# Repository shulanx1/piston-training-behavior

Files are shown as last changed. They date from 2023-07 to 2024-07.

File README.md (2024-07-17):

# README #

* Behavioral training set up for two whisker discrimination task based on pneumetic whisker stimulation

### Python environment Requirement: ###
* numpy
* scipy
* playsound
* pyserial

### Hardware on the circuit board: ###
* 24 V piston air pressure regulator: https://www.smcpneumatics.com/V114T-5LZ-M5.html
* 24 VDC power relay: digikey 255-5324-5-ND
* dual channel diod: digikey 1655-BAT54CCT-ND
* dual channel NTN transister: digikey MBT3904DW1T1G
* 12 V water valve: Nresearch 161K011 or thevalveshop 411L3112HV https://www.thevalveshop.com/menu/auto/asco/asco-scientific.html 
* 12 V water valve driver: Nresearch 161D1X250
* 5V speaker (with amplifier): digikey 1528-1746-ND
* vibration motor: 3V
* stepper motor: Makeblock Me Stepper Motor Driver https://amicus.com.sg/shop/makeblock/me-stepper-motor-driver/
* rotary encoder: https://www.usdigital.com/products/encoders/incremental/rotary/shaft/H5
* piezo based lickometer:<br />
single-rail op-amp: TLV2771CDBVR<br />
shunt regulator: ATL431BQDBZR<br />
non-inverting svhmitt trigger: SN74LVC1G17DBVR<br />
LED: 160-1183-1-ND<br />
trimmer resistor: digikey 3362P-504LF-ND<br />
* piezo based lickometer (with rail splitter:<br />
op-amp: TLV2371IDBVR<br />
rail splitter: TLE2426QDRG4Q1 <br />
cap 200nF: 1189-2375-ND  <br />
cap 1uF: 399-ESS105M050AB2EACT-ND <br\>

### pin layout V6 ###
* D2: capacitance/piezo lick sensor
* D3: water valve
* D5, D6: rotary encoder (A,B)
* D8, D9, D11, D12: piston
* D10: sliding switch (start trigger)
* A1, A2: LED/conductance lick sensor
* A3: speaker
* D11, D7: stepper motor (STP, DIR)
* D4, D12: vibrating piezo

### pin layout V7 ###
* D2: capacitance/piezo lick sensor
* D3: water valve
* D4: sliding switch (start trigger)
* D5, D6, A2: rotary encoder (A,B,rotations)
* D8, D9, A4, A5: piston
* A1: LED/conductance lick sensor
* A3: speaker
* A5, A4: stepper motor (STP, DIR)

### Files ###

* //BehavioralPCB: arduino code to upload to arduino uno (board V6)
* //Bonsai lick detection: real time lick detection with webcam when capactive based lick sensor causes electrical artifact
* //training.py: training file to serial communicate with arduino
* //behavior_training_decode: matlab file to decode the serial output of arduino
* //Arduino_board_V6: PCB design
* //CAD: laser engraving pattern on the running disk

### Install ###
* Arduino: <br />
At sketch -> include library -> add .zip library, add the dio2.zip folder<br />

* Python: <br />
on the command window, run: <br />
-- pip install playsound <br />
-- pip install pyserial <br />

### To start the training from command window ###
-- cd path-to-base-folder <br />
-- python training.py COM12 ear-tag-number phase <br />

### Training phase ###
* 1: no whisker stim, reward dispense when the lick is detected
* 2: GO and NOGO stim, with teaching signal
* 3: GO and NOGO stim, reward is given at "hit", time out at false alarm
* 4: optogenetic stimulation in randomly chosen half of the trials,  reward is given at "hit", time  out at false alarm

### Arduino test serial command ###
* 'v': test valve
* 'p': test pistons
* 'c': test cue sound
* 'f': flush the valve
* 'g': GO piston, use the sliding switch to turn on and off
* 'n': NOGO piston, use the sliding switch to turn on and off

### Arduino serial output row ###
* 1: rotary decoder
* 2: licking
* 3: valve
* 4: GO piston
* 5: NOGO piston
* 6: hit rate
* 7: false alarm rate
* 8: time

### Arduino pin map ###
* DO2: lick sensor
* DO3: valve
* DO5&DO6: rotary encoder
* D8, D9, D12, D12: pistons
* D10: sliding switch
* D13: trigger

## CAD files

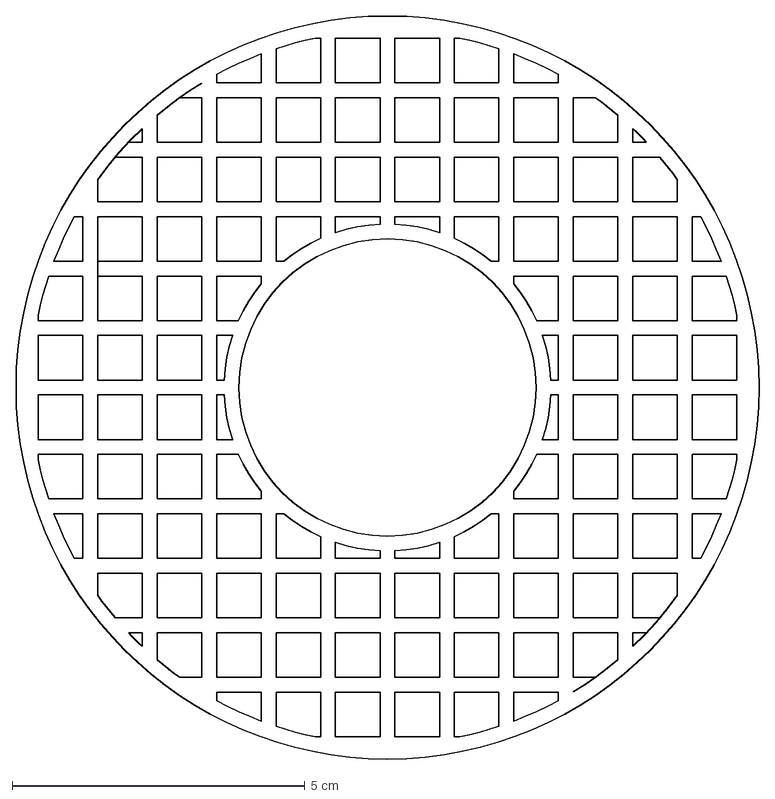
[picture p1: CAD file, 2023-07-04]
CAD/wheel v4.dxf
12.7 x 12.7 cm

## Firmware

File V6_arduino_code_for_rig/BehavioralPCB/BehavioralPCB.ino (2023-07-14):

/* Read Quadrature Encoder
   Connect Encoder to Pins encoder0PinA, encoder0PinB, and +5V.

*/
//print sequence: rundist, lick, valve, pistonGO, pisktonNOGO, time

#include <arduino2.h>

int val;
const int lick_sensor = 2;
const int valve_enable = 3;
const int pistonGO = 8;
const int output_trig = 13;
const int pistonNOGO = 9;
int encoder0PinA = 6;
int encoder0PinB = 5;
//int encoder0Pos = 0;
long int encoder0PosTot = 0;
int encoder0PinALast = LOW;
int n = LOW;
int count = 0;
int counter = 250;
int LED1 = A1;
int audio = A3;
int trigger = 10;
int lick_state = 0;
int valve_state = 0;
int go_stim_state = 0;
int nogo_stim_state = 0;
int go_teach = 0;
int nogo_teach = 0;
int previousState = LOW;
int piston_test_previousState = LOW;
int LED2 = A2;
int flag = 0;
int piston_test_flag = 0;
const int respond_window = 1000;  // time window (ms) after sensory stimuli that if lick is detected reward will be given
const int baseline_time = 3000;  // duration of baseline aquisition before trial starts
const int poststim_time = 4000;
const int reward_dur = 35;   // duration (ms) of reward
const int stim_dur = 4000; // time duration (ms) of sensory stimuli
const int time_out_dur = 15000;  // time out duration (ms)
const int wait_dur = 800;    //1000-sample time (us)
const int teach_dur = 10000; // small time out after teach signal, if lick happens during the time, considered as hit
float teach_ratio = 1.0;  //if correct detection/rejection is lower than teach ratio, send a teaching signal
const int previous_state_num = 10; //average the performance of previous numbers of trials to generate teach signals
unsigned int previous_go_performance = 992; //0x03e0
unsigned int previous_nogo_performance = 31;  //0x001f
unsigned int hit_trials = 0;
unsigned int fa_trials = 0;
unsigned int GO_trials = 0;
unsigned int NOGO_trials = 0;
float hit_rate = 0.0;
float fa_rate = 0.0;
const unsigned int update_shift = 15360; // 0x3c00, inverse the first 3rd to 6th digit, so the updated value is not the same as before 

const int cue_f = 2000;
const int cue_fs = 20000;
float cue_samples[100];
unsigned int cue_interval = 1000000/cue_fs;

int sampEncoderPos = 0;
int sampEncoderPosPrev = 0;
int changePos = 0;
unsigned long sampTime = 0;
int encoder_flag = 0;
float totalPos = 0;
const int fs_encoder = 100; // the sampling frequency of the encoder 

unsigned long microsStart;
unsigned long microsFix;
unsigned long deltaT;
float convertPos;

void setup() {
  Serial.begin(115200);  
//  Serial.setTimeout(1);
  while (!Serial) {
    //wait for serial port to open
  }
  pinMode (output_trig, OUTPUT);
  pinMode (encoder0PinA, INPUT);
  pinMode (encoder0PinB, INPUT);
  pinMode (lick_sensor, INPUT);
  pinMode (valve_enable, OUTPUT);
  pinMode (pistonGO, OUTPUT);
  pinMode (pistonNOGO, OUTPUT);
  pinMode (trigger, INPUT);
  pinMode (LED1, OUTPUT);
  pinMode(LED2,OUTPUT);
  pinMode(audio, OUTPUT);
  digitalWrite2(valve_enable,LOW);
  digitalWrite2(pistonGO, LOW);
  digitalWrite2(pistonNOGO, LOW);
  digitalWrite2(output_trig, LOW);

  float cue_time = 0.0;
  int cue_cycle = (int) (cue_fs/cue_f);
  for (int n = 0; n < cue_cycle; n++){
    cue_time = (float) n/cue_cycle;
    cue_samples[n] = (float)(127.0*sin(2*3.14*cue_time)+127.0);
  }  

  cli(); // stop interrupts
  
  // set TIMER1 interrupt at 2kHz
  TCCR1A = 0;// set entire TCCR1A register to 0
  TCCR1B = 0;// same for TCCR1B
  TCNT1  = 0;//initialize counter value to 0
  // set compare match register for 0.5kHz increments
  OCR1A  = 19999; //(16*10^6) / (fs_encoder*8) - 1 //(must be <65536)
  // turn on CTC mode
  TCCR1B |= (1 << WGM12);
  // Set CS10 and CS12 bits for 8 prescaler
  TCCR1B |= (1 << CS11) | (0 << CS10);  
  // enable timer compare interrupt
  TIMSK1 |= (1 << OCIE1A); 

  sei(); // allow interrupts

  previousState = digitalRead2(trigger);
  microsStart=micros();
  flag = 0;
  Serial.print("Ready");
}

void loop() {
  if((previousState == LOW) && (digitalRead2(trigger) == HIGH)){
    flag = 1;
    digitalWrite2(LED2,HIGH);
    microsFix = micros();
    previousState = HIGH;
    Serial.print("start");
    Serial.print("\n");
    while (!Serial.available());
    char a = Serial.read();
    teach_ratio = int (a-'0')/10.0;    
//    Serial.print(teach_ratio);
//    Serial.print('\n');    
    serialFlush();

  }
  else if((previousState == HIGH) && (digitalRead2(trigger) == LOW)){
      flag = 0;
      digitalWrite2(LED2,LOW);
      convertPos = 0;
      totalPos = 0;
      encoder0PosTot = 0;
      hit_trials = 0;
      fa_trials = 0;
      GO_trials = 0;
      NOGO_trials = 0;
      hit_rate = 0.0;
      fa_rate = 0.0;
      
      previousState = LOW;
      teach_ratio = 1;
  }

  if (flag == 1){
    if (Serial.available() > 0){
      char a = Serial.read();
      switch(a)
      {
        case '0':   // reward given whenever lick happens
          if (digitalRead2(lick_sensor) == HIGH){
            lick_state = 1;
            valve_state = 1;
            digitalWrite2(valve_enable, HIGH);
            delay(reward_dur);
            digitalWrite2(valve_enable, LOW);
            rotary_decode();
            valve_state = 0;
            while (digitalRead2(lick_sensor)==HIGH){
              delay(5);
              lick_state = 1;
              rotary_decode();
          } 
          }
          lick_state = 0;
          valve_state = 0;
          rotary_decode();
          break;

        case '1':   
        /* GO stimuli, 
        if the average mistake in the previous 10 trials larger than 0.5, give reward regardless of licking, 
        otherwise, reward only when licking */
          digitalWrite2(output_trig, LOW);
          GO_trials = GO_trials + 1;
          count = 0;
            while (count < baseline_time){
            if (digitalRead2(lick_sensor)==HIGH){
              lick_state = 1;
            }
            else{lick_state = 0;}
            rotary_decode();
            delayMicroseconds(wait_dur);
            count = count + 1;
          }   //baseline
          count = 0;
          digitalWrite2(pistonGO, HIGH);
          go_stim_state = 1;
          count = 0;
          delay(10); // time for piston response
          previous_go_performance = ((previous_go_performance << 1) ^ update_shift) & 16383; // left shift, inverse 3rd to 6th digit, zero 1st &2nd digit
          while (count < stim_dur-10){
            if (digitalRead2(lick_sensor)==HIGH){
              lick_state = 1;
              previous_go_performance = previous_go_performance | 1;
            }
            else{
              lick_state = 0;
            }
            rotary_decode();
            delayMicroseconds(wait_dur);
            count = count + 1;
          }
          digitalWrite2(pistonGO, LOW);
          go_stim_state = 0;         
          if (previous_go_performance & 1 == 1){
            hit_trials = hit_trials + 1;
            rotary_decode();
            valve_state = 1;
            digitalWrite2(valve_enable, HIGH);
            delay(reward_dur);
            digitalWrite2(valve_enable, LOW);  
            rotary_decode();
            hit_rate = (float) hit_trials/GO_trials;
          }
          else {
          go_teach_signal();
          hit_rate = (float) hit_trials/GO_trials;
          if ((go_teach == 1)){
            rotary_decode();
            valve_state = 1;
            digitalWrite2(valve_enable, HIGH);
            delay(reward_dur);
            digitalWrite2(valve_enable, LOW);   
            rotary_decode();
            previous_go_performance = previous_go_performance | (1 << 15);
            while (count < teach_dur){ // small time out session after teach signal
              if (digitalRead2(lick_sensor)==HIGH){
                lick_state = 1;
                previous_go_performance = previous_go_performance | 1;
                //hit_rate = (float) (hit_trials+1)/GO_trials;
              }
              else{lick_state = 0;}
            rotary_decode();
            delayMicroseconds(wait_dur);
            count = count + 1;
            }
            if (previous_go_performance & 1 == 1){
              hit_trials = hit_trials + 1;
            }
            hit_rate = (float) (hit_trials)/GO_trials;
            serialFlush();
          }
            }
                
          rotary_decode(); 
          
          lick_state = 0;
          count = 0;
            while (count < poststim_time){
            if (digitalRead2(lick_sensor)==HIGH){
              lick_state = 1;
            }
            else{lick_state = 0;}
            rotary_decode();
            delayMicroseconds(wait_dur);
            count = count + 1;
          }   //baseline
          valve_state = 0;  
          digitalWrite2(output_trig, LOW);
          
          break;
        
        case '7':   
        /* NOGO stimuli, 
        if the average mistake in the previous 10 trials larger than 0.5, no time out regardless of licking, 
        otherwise, timeout when licking */
          NOGO_trials = NOGO_trials + 1;
          digitalWrite2(output_trig, HIGH);
          count = 0;
            while (count < baseline_time){
            if (digitalRead2(lick_sensor)==HIGH){
              lick_state = 1;
            }
            else{lick_state = 0;}
            rotary_decode();
            delayMicroseconds(wait_dur);
            count = count + 1;
          }   //baseline
          digitalWrite2(pistonNOGO, HIGH);

          nogo_stim_state = 1;
          count = 0;
          delay(10); // time for piston response
          previous_nogo_performance = ((previous_nogo_performance << 1) ^ update_shift) & 16383;
          while (count < stim_dur-10){
            if (digitalRead2(lick_sensor)==HIGH){
              lick_state = 1;
              previous_nogo_performance = previous_nogo_performance | 1;
            }
            else{lick_state = 0;}
            rotary_decode();
            delayMicroseconds(wait_dur);
            count = count + 1;
          }

          digitalWrite2(pistonNOGO, LOW);
          nogo_stim_state = 0;
          // count = 0;
          // while (count < respond_window){
          //   if (lick_state == 1){
          //     break;
          //   }
          //   else{
          //     if (digitalRead2(lick_sensor) == HIGH){
          //       rotary_decode();
          //       lick_state = 1;
          //       break;
          //     }
          //     rotary_decode();
          //     delayMicroseconds(wait_dur);
          //     count = count + 1;  
          //   }        
          // }
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

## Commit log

2023-04-24 updated with teaching signal in training
    [Arduino_shield-B_Mask.gbr, Arduino_shield-B_SilkS.gbr, Arduino_shield-Bottom.gbr, Arduino_shield-Edge_Cuts.gbr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]
2023-07-04 change the arduino output
    [Arduino_shield-B_Mask.gbr, Arduino_shield-B_SilkS.gbr, Arduino_shield-Bottom.gbr, Arduino_shield-Edge_Cuts.gbr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]
2024-07-17 added V7 board with SD card slot
    [Arduino_shield-B_Mask.gbr, Arduino_shield-B_SilkS.gbr, Arduino_shield-Bottom.gbr, Arduino_shield-Edge_Cuts.gbr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]
